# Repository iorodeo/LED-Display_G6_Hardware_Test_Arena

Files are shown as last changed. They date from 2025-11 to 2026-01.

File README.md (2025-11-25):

## LED-Display\_G6\_Hardware\_Test\_Arena 

This repository is part of <https://reiserlab.github.io/Modular-LED-Display/>.
It contains the KiCad design and production files for the G6 panel test arena
hardware. 

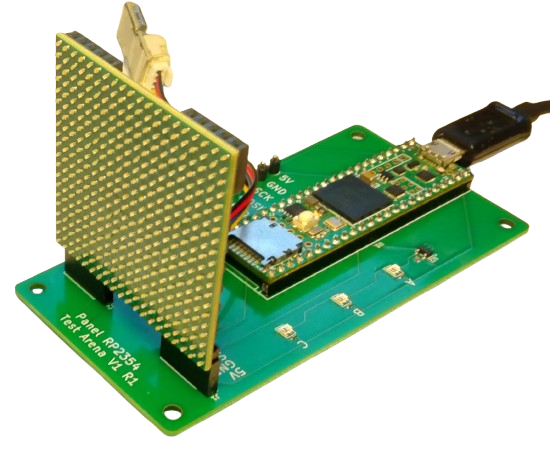
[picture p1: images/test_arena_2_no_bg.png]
image 1 of teensy test arena


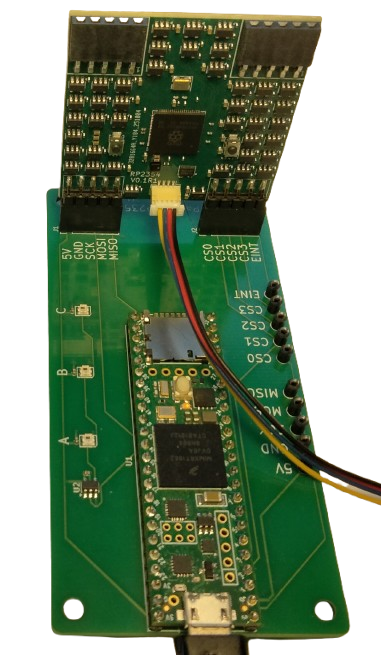
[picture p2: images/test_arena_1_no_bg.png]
image 1 of teensy test arena


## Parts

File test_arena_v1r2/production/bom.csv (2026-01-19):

Designator | Footprint | Quantity | Value | LCSC Part #
C1, C2, C3, C4, C5, C6, C7, C8 | 0402 | 8 | 100nF | C1525
C9 | 1210 | 1 | 100uF | C84455
D1, D2, D3 | LED_WS2812B-2020_PLCC4_2.0x2.0mm | 3 | WS2812B-2020 | C965555
J1, J2 | PinSocket_1x05_P2.54mm_Vertical | 2 | Conn_01x05_Socket | C50950
JP1 | PinHeader_1x02_P2.54mm_Vertical | 1 | Jumper_2_Open | C492401
R1, R10, R11, R12, R2, R3, R4, R5, R6, R7, R8, R9 | 0402 | 12 | 33 | C25105
TP1, TP10, TP11, TP12, TP2, TP3, TP4, TP5, TP6, TP7, TP8, TP9 | TestPoint_THTPad_D2.0mm_Drill1.0mm | 12 | TestPoint | C238122
U2 | SOT-23-5 | 1 | SN74LV1T34DBV | C100024
U3, U4, U5, U6 | SOT-23-6 | 4 | 74LVC2G17 | C10429

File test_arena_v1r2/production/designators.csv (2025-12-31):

C1:1
C2:1
C3:1
C4:1
C5:1
C6:1
C7:1
C8:1
C9:1
D1:1
D2:1
D3:1
H1:1
H2:1
H3:1
H4:1
J1:1
J2:1
J3:1
JP1:1
R1:1
R10:1
R11:1
R12:1
R2:1
R3:1
R4:1
R5:1
R6:1
R7:1
R8:1
R9:1
TP1:1
TP10:1
TP11:1
TP12:1
TP2:1
TP3:1
TP4:1
TP5:1
TP6:1
TP7:1
TP8:1
TP9:1
U1:1
U2:1
U3:1
U4:1
U5:1
U6:1

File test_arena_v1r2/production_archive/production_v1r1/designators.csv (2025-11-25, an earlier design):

C1:1
C2:1
C3:1
C4:1
D1:1
D2:1
D3:1
H1:1
H2:1
H3:1
H4:1
J1:1
J2:1
TP1:1
TP10:1
TP2:1
TP3:1
TP4:1
TP5:1
TP6:1
TP7:1
TP8:1
TP9:1
U1:1
U2:1

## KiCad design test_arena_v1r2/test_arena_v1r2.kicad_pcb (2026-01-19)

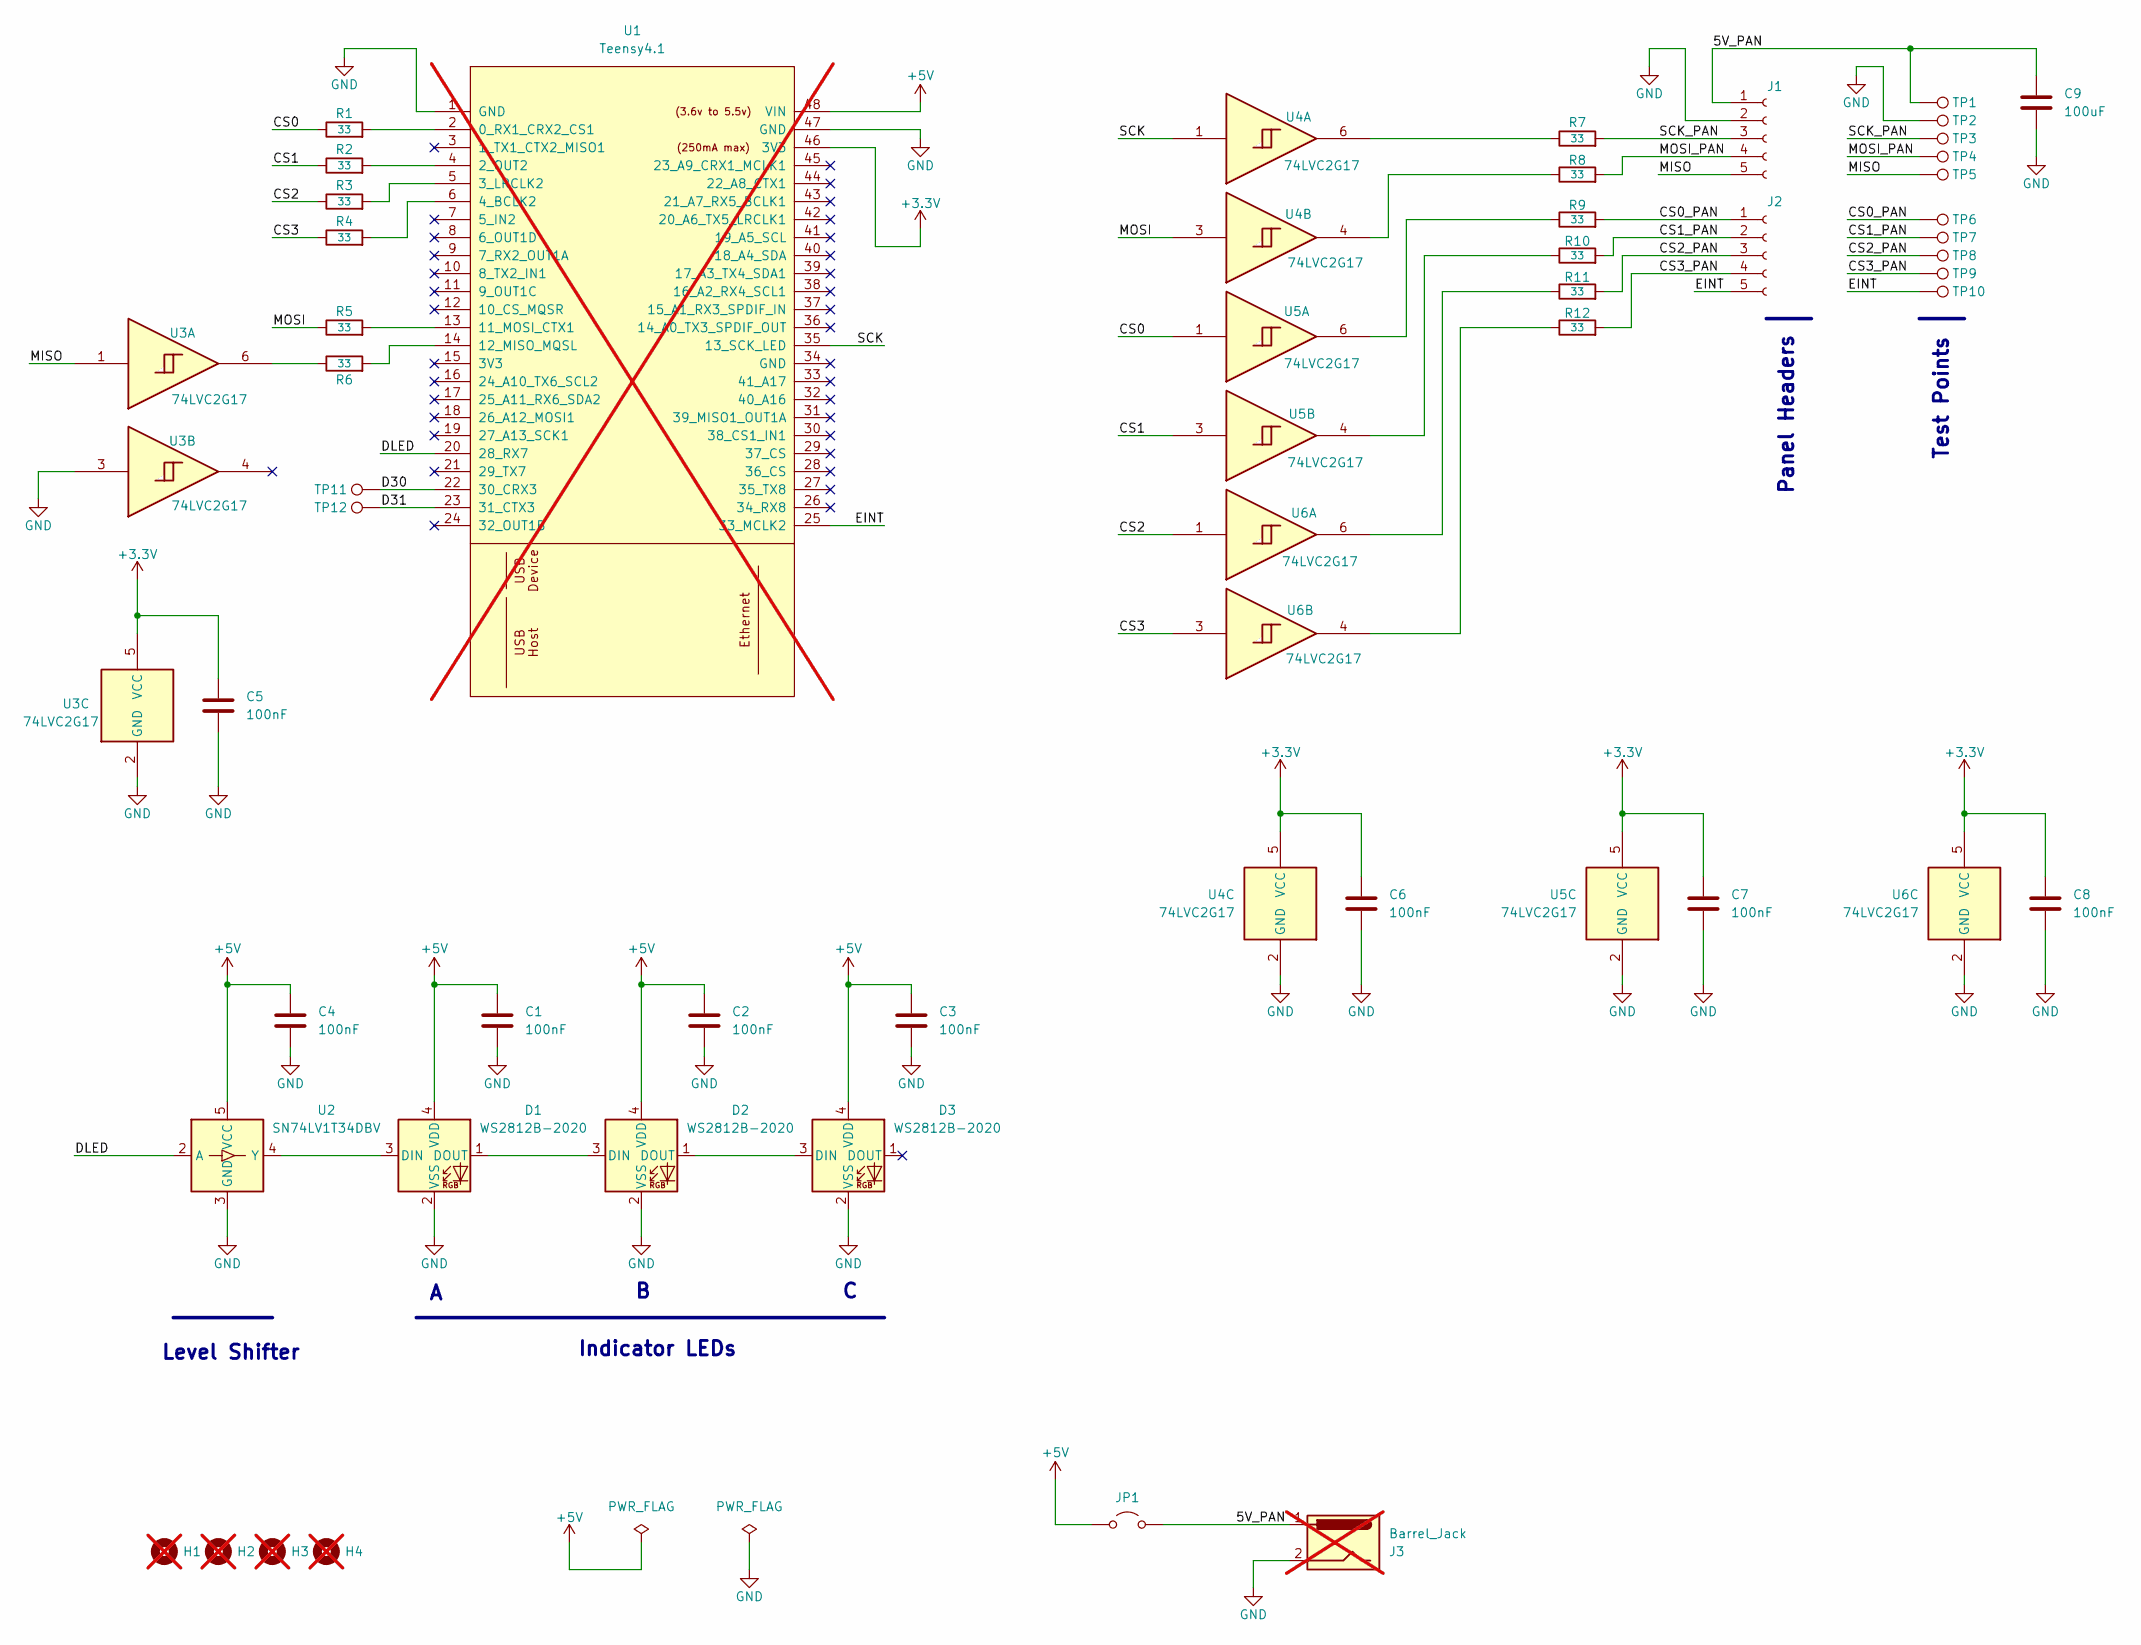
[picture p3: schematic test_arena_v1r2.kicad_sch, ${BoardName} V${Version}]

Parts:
C1, C2, C3, C4, C5, C6, C7, C8: 100nF; C_0402_1005Metric; LCSC Part # C1525
C9: 100uF; C_1210_3225Metric; LCSC Part # C84455
D1, D2, D3: WS2812B-2020; LED_WS2812B-2020_PLCC4_2.0x2.0mm; LCSC Part # C965555
H1, H2, H3, H4: MountingHole; MountingHole_3.2mm_M3; not fitted
J1, J2: Conn_01x05_Socket; PinSocket_1x05_P2.54mm_Vertical; LCSC Part # C50950
J3: Barrel_Jack; DCJACK_2PIN_HIGHCURRENT; not fitted
JP1: Jumper_2_Open; PinHeader_1x02_P2.54mm_Vertical; LCSC Part # C492401
R1, R2, R3, R4, R5, R6, R7, R8, R9, R10, R11, R12: 33; R_0402_1005Metric; LCSC Part # C25105
TP1, TP2, TP3, TP4, TP5, TP6, TP7, TP8, TP9, TP10, TP11, TP12: TestPoint; TestPoint_THTPad_D2.0mm_Drill1.0mm; LCSC Part # C238122
U1: Teensy4.1; Teensy41_outer_only; not fitted
U2: SN74LV1T34DBV; SOT-23-5; LCSC Part # C100024
U3, U4, U5, U6: 74LVC2G17; SOT-23-6; LCSC Part # C10429

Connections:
+3.3V: C5.1, C6.1, C7.1, C8.1, U1.46 (3V3), U3.5 (VCC), U4.5 (VCC), U5.5 (VCC), U6.5 (VCC)
+5V: C1.1, C2.1, C3.1, C4.1, D1.4 (VDD), D2.4 (VDD), D3.4 (VDD), JP1.1 (A), U1.48 (VIN), U2.5 (VCC)
/5V_PAN: C9.1, J1.1, J3.1, JP1.2 (B), TP1.1
/CS0: R1.1, U5.1
/CS0_PAN: J2.1, R9.2, TP6.1
/CS1: R2.1, U5.3
/CS1_PAN: J2.2, R10.2, TP7.1
/CS2: R3.1, U6.1
/CS2_PAN: J2.3, R11.2, TP8.1
/CS3: R4.1, U6.3
/CS3_PAN: J2.4, R12.2, TP9.1
/D30: TP11.1, U1.22 (30_CRX3)
/D31: TP12.1, U1.23 (31_CTX3)
/DLED: U1.20 (28_RX7), U2.2 (A)
/EINT: J2.5, TP10.1, U1.25 (33_MCLK2)
/MISO: J1.5, TP5.1, U3.1
/MOSI: R5.1, U4.3
/MOSI_PAN: J1.4, R8.2, TP4.1
/SCK: U1.35 (13_SCK_LED), U4.1
/SCK_PAN: J1.3, R7.2, TP3.1
GND: C1.2, C2.2, C3.2, C4.2, C5.2, C6.2, C7.2, C8.2, C9.2, D1.2 (VSS), D2.2 (VSS), D3.2 (VSS), J1.2, J3.2, TP2.1, U1.1 (GND), U1.47 (GND), U2.3 (GND), U3.2 (GND), U3.3, U4.2 (GND), U5.2 (GND), U6.2 (GND)
unnamed: D1.3 (DIN), U2.4 (Y)
unnamed: D1.1 (DOUT), D2.3 (DIN)
unnamed: D2.1 (DOUT), D3.3 (DIN)
unnamed: R6.1, U3.6
unnamed: R7.1, U4.6
unnamed: R8.1, U4.4
unnamed: R9.1, U5.6
unnamed: R10.1, U5.4
unnamed: R11.1, U6.6
unnamed: R12.1, U6.4
unnamed: R1.2, U1.2 (0_RX1_CRX2_CS1)
unnamed: R2.2, U1.4 (2_OUT2)
unnamed: R3.2, U1.5 (3_LRCLK2)
unnamed: R4.2, U1.6 (4_BCLK2)
unnamed: R5.2, U1.13 (11_MOSI_CTX1)
unnamed: R6.2, U1.14 (12_MISO_MQSL)

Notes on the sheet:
Test Points
Indicator LEDs
Panel Headers
Level Shifter

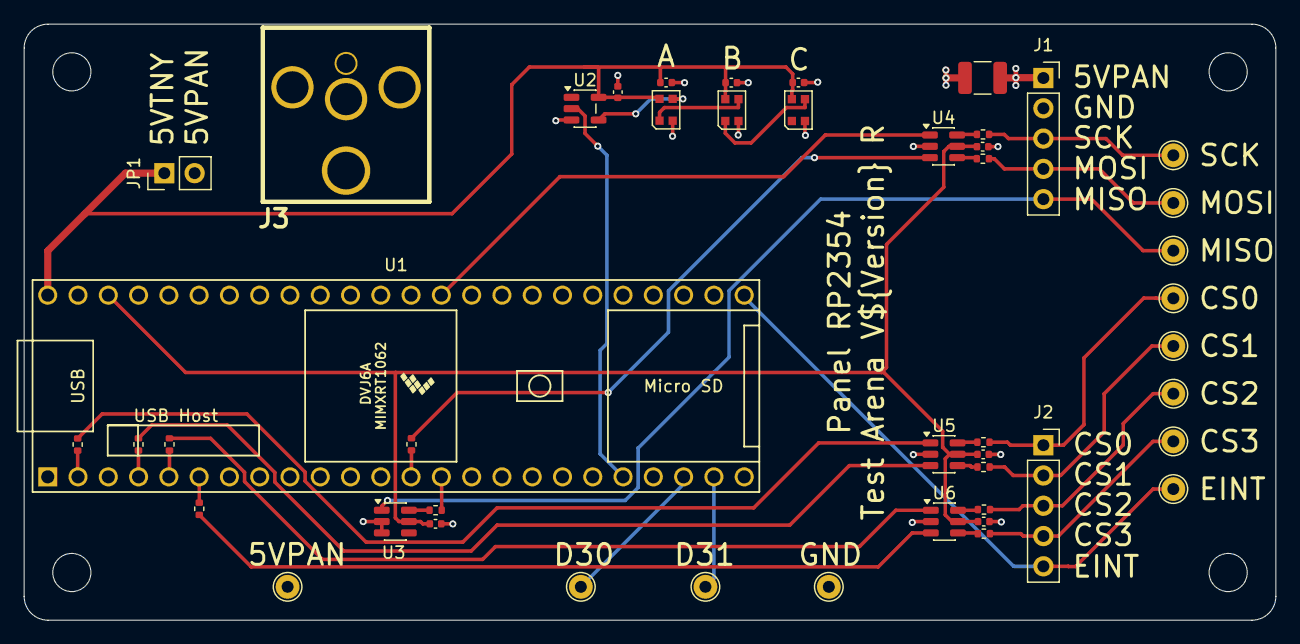
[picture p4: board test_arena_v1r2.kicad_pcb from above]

Board: 4 copper layers, 105.0 x 50.0 mm, 50 parts (0 on the bottom side), 37 nets.

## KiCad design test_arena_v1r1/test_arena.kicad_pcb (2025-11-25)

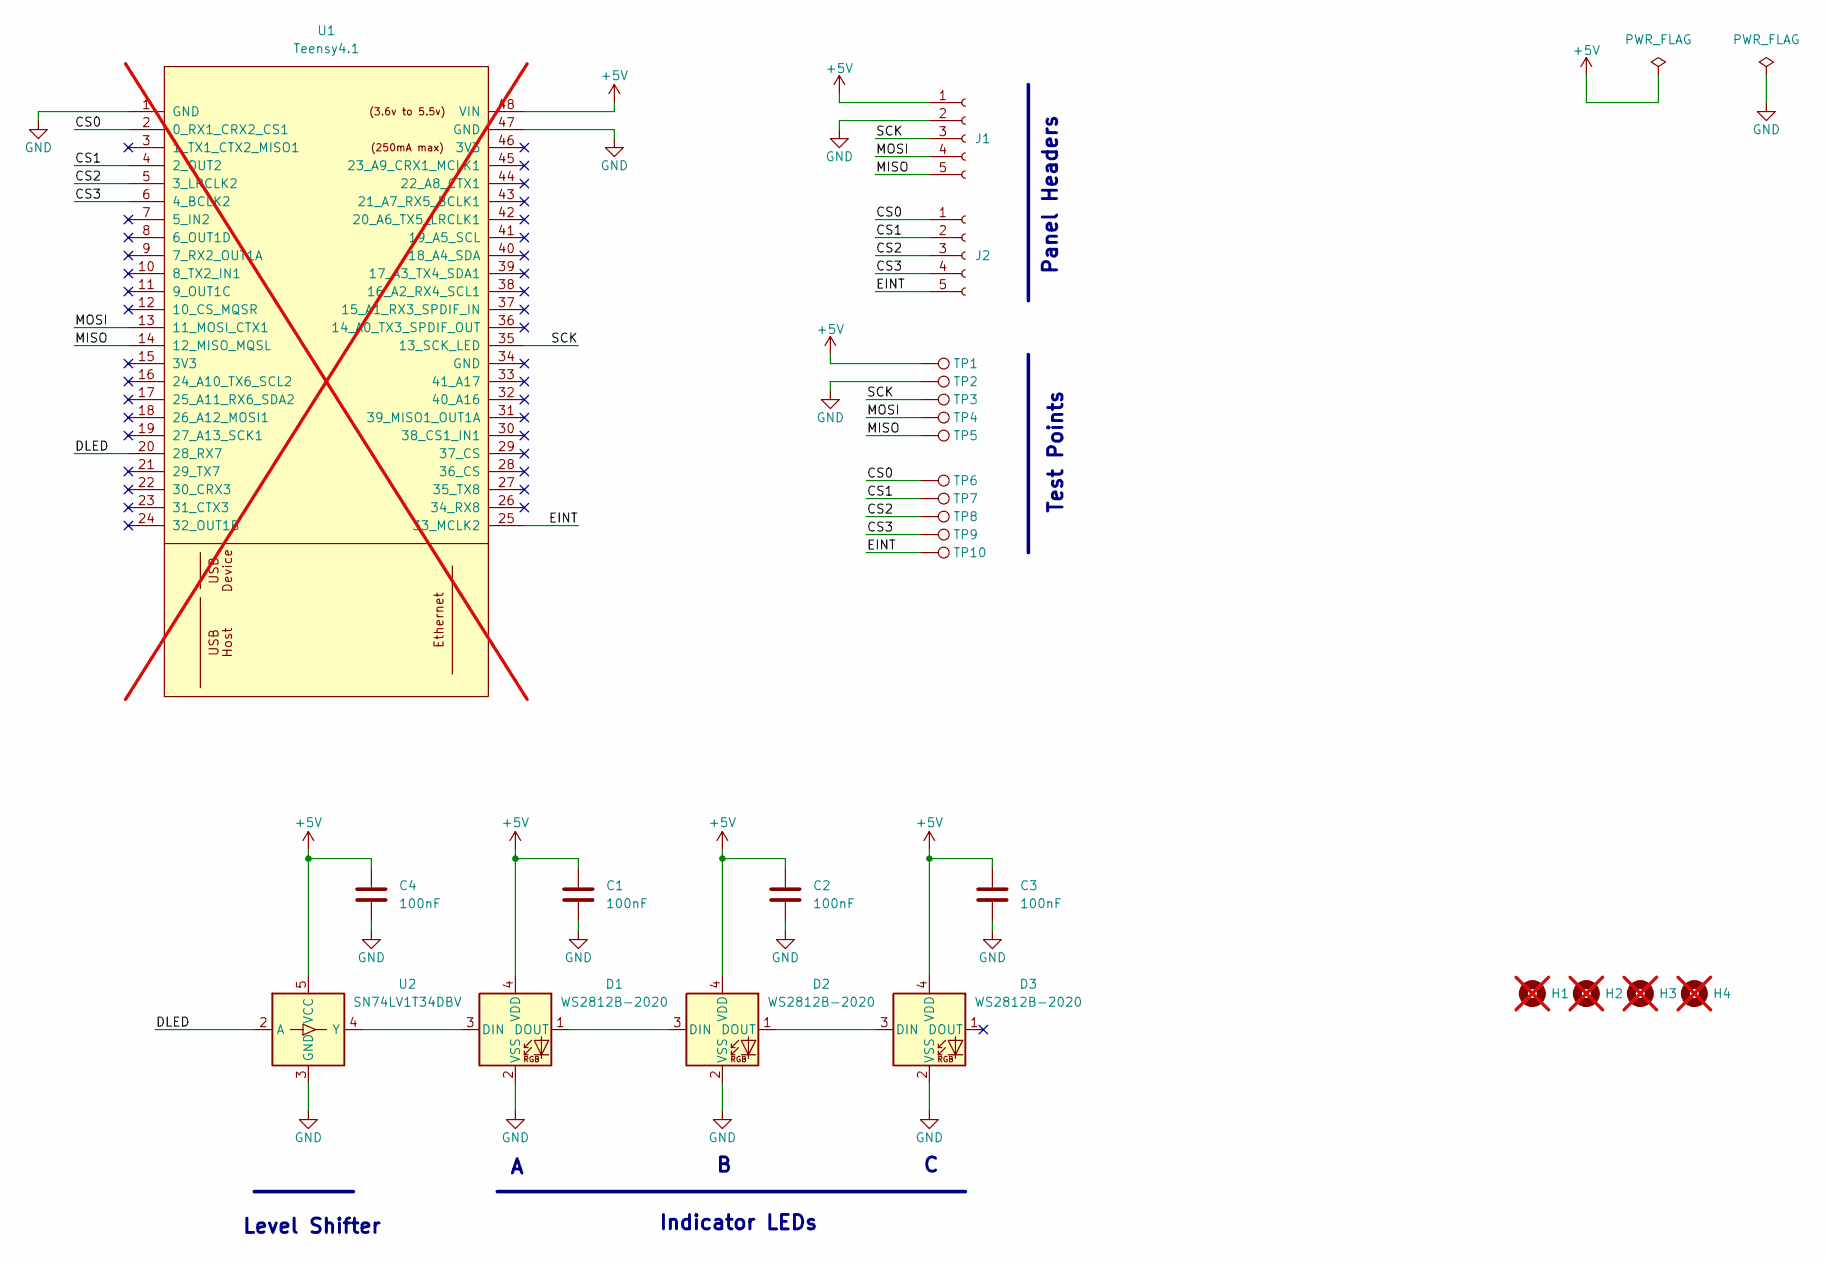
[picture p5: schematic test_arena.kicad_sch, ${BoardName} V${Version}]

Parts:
C1, C2, C3, C4: 100nF; C_0402_1005Metric; LCSC Part # C1525
D1, D2, D3: WS2812B-2020; LED_WS2812B-2020_PLCC4_2.0x2.0mm; LCSC Part # C965555
H1, H2, H3, H4: MountingHole; MountingHole_3.2mm_M3; not fitted
J1, J2: Conn_01x05_Socket; PinHeader_1x05_P2.54mm_Vertical; LCSC Part # C50950
TP1, TP2, TP3, TP4, TP5, TP6, TP7, TP8, TP9, TP10: TestPoint; TestPoint_THTPad_D2.0mm_Drill1.0mm; LCSC Part # C238122
U1: Teensy4.1; Teensy41_outer_only; not fitted
U2: SN74LV1T34DBV; SOT-23-5; LCSC Part # C100024

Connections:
+5V: C1.1, C2.1, C3.1, C4.1, D1.4 (VDD), D2.4 (VDD), D3.4 (VDD), J1.1, TP1.1, U1.48 (VIN), U2.5 (VCC)
/CS0: J2.1, TP6.1, U1.2 (0_RX1_CRX2_CS1)
/CS1: J2.2, TP7.1, U1.4 (2_OUT2)
/CS2: J2.3, TP8.1, U1.5 (3_LRCLK2)
/CS3: J2.4, TP9.1, U1.6 (4_BCLK2)
/DLED: U1.20 (28_RX7), U2.2 (A)
/EINT: J2.5, TP10.1, U1.25 (33_MCLK2)
/MISO: J1.5, TP5.1, U1.14 (12_MISO_MQSL)
/MOSI: J1.4, TP4.1, U1.13 (11_MOSI_CTX1)
/SCK: J1.3, TP3.1, U1.35 (13_SCK_LED)
GND: C1.2, C2.2, C3.2, C4.2, D1.2 (VSS), D2.2 (VSS), D3.2 (VSS), J1.2, TP2.1, U1.1 (GND), U1.47 (GND), U2.3 (GND)
unnamed: D1.3 (DIN), U2.4 (Y)
unnamed: D1.1 (DOUT), D2.3 (DIN)
unnamed: D2.1 (DOUT), D3.3 (DIN)

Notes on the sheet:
Test Points
Indicator LEDs
Panel Headers
Level Shifter

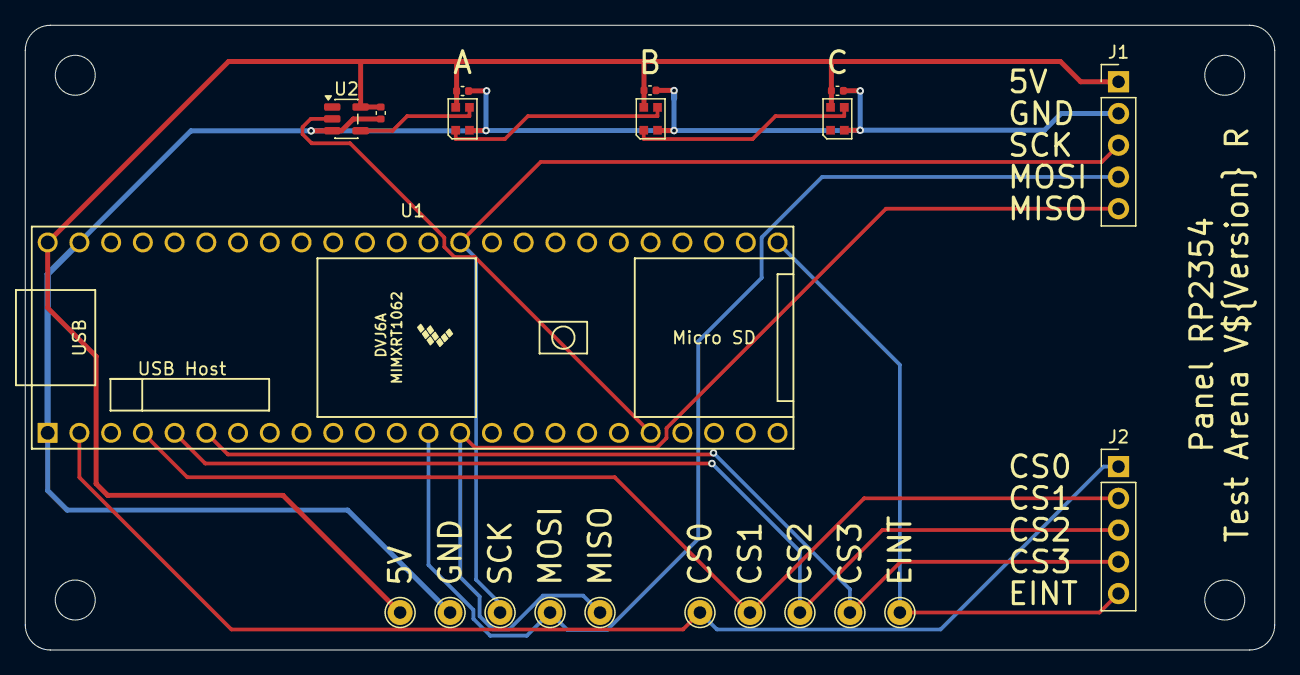
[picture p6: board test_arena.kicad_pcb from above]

Board: 2 copper layers, 100.0 x 50.0 mm, 25 parts (0 on the bottom side), 14 nets.

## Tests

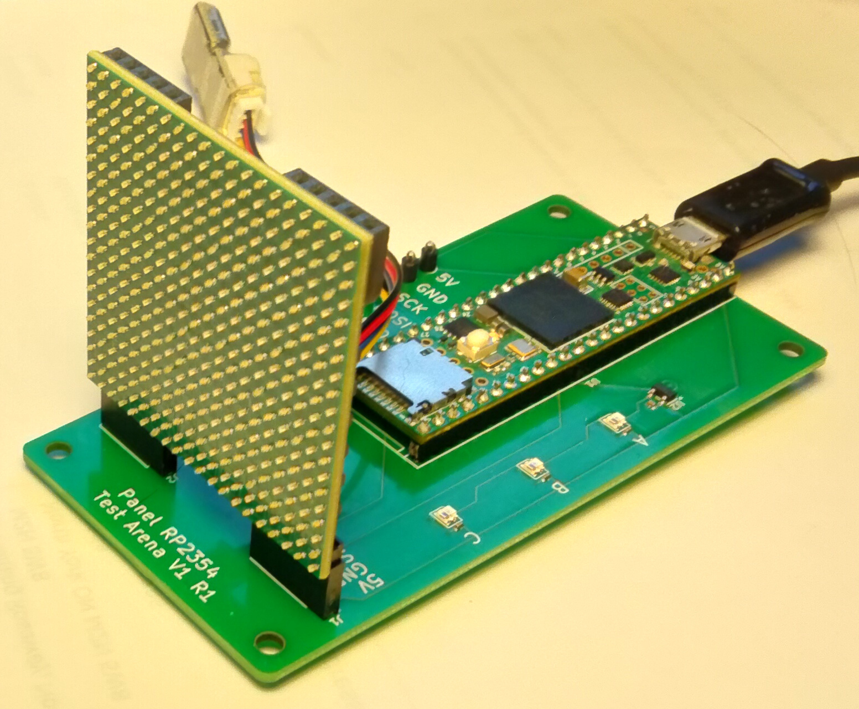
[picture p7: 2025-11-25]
images/test_arena_2.png

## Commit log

2025-11-25 Project creation.
    [bom.csv, designators.csv, positions.csv, test_arena-B_Cu.gbl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]
2025-11-25 Added production archive.
    [bom.csv, designators.csv, positions.csv, test_arena-B_Cu.gbl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]
2025-12-17 Added modified V0.1 R1 test arena design.
    This design incorporates the same SPI signal handling as is
    planned for the 10-ring arena.
    [bom.csv, designators.csv, positions.csv, test_arena_pwr_gnd_route.kicad_pcb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]
2025-12-18 Added final design for modified test arena.
    [test_arena_pwr_gnd_route.kicad_pcb, test_arena_v1r2.dsn, test_arena_v1r2.kicad_pcb, test_arena_v1r2.kicad_sch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]
2025-12-31 Added production files for v1r2 test arena.
    [bom.csv, designators.csv, positions.csv, test_arena_v1r2.kicad_pcb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]
2026-01-19 Fixed wrong part issue on v1r2 test arena.
    [bom.csv, test_arena_v1r2.kicad_pcb, test_arena_v1r2.kicad_sch]
